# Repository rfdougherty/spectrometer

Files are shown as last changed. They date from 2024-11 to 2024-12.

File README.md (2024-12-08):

# Spectrometer

An Arduino-based controller for the [Hamamatsu C12880MA](https://www.hamamatsu.com/us/en/product/optical-sensors/spectrometers/mini-spectrometer/C12880MA.html) mini spectrometer using the [ESP32-S3](https://www.espressif.com/en/products/socs/esp32-s3) microcontroller. The figure below shows measurements of daylight entering a window across a 2-hour period just a little after noon in Redwood City California on October 26th, 2024. A simple auto-integration time algorithm was used so the raw voltage readings were scaled by the integration time to show the luminance differences between readings as the sun moved across the sky. (See [examples/spectrum.ipynb](examples/spectrum.ipynb) for the code used to make this plot.)

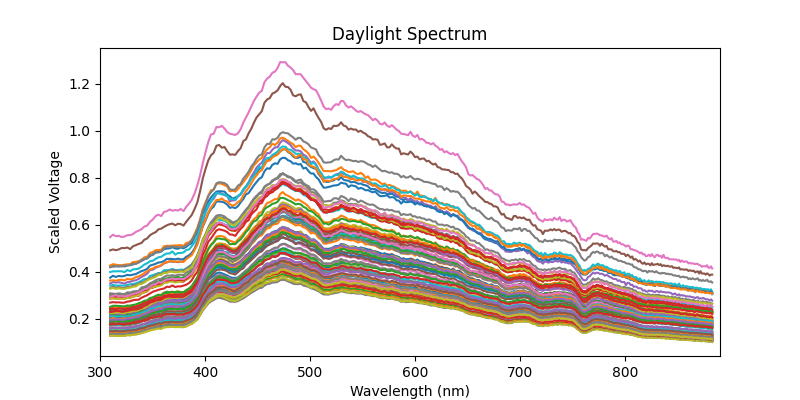
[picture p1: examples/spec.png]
example spectrum


## Overview

This project includes firmware for controlling the Hamamatsu C12880 mini spectrometer, offering web-based remote control and data acquisition. The system includes temperature and humidity monitoring via an AHT10 sensor. The device is very portable and easily powered for days using a small usb power bank, allowing longitudinal measurements in the field (e.g., to measure the daylight variation in a particular location).

### Features

- Web server interface for spectrometer control
- Over-the-Air (OTA) firmware updates
- WiFi configuration via WiFiManager
- Temperature and humidity data
- Wavelength calibration (be sure to update the coefficients in [getWavelength](firmware/firmware.ino) with the values from your calibration certificate!)
- NTP time synchronization for precise timestamping of measurements
- Status LED indicator

### Integration time

A spectrometer's integration time is the length of time it takes to collect photons and accrue charge on the sensor. It must be adjusted to maximize the signal-to-noise by using the full range of the sensor's analog output while avoiding saturation of any of the pixels. The current firmware does not include an automatic integration time algorithm, so the integration time must be manually set when you call the API to get a reading. The [examples/spectrum.ipynb](examples/spectrum.ipynb) notebook includes an example of how to use the API to automatically select an integration time by making multiple API calls with different integration times to find a value just below the sensor's saturation point.

## Hardware

- **Microcontroller**: ESP32-S3 (e.g., [LOLIN S3 mini](https://www.wemos.cc/en/latest/s3/s3_mini.html))
- **Spectrometer**: [Hamamatsu C12880MA](https://www.hamamatsu.com/us/en/product/optical-sensors/spectrometers/mini-spectrometer/C12880MA.html)
- **Temperature/Humidity Sensor**: AHT10/AHT20 (e.g., [this module](https://www.amazon.com/gp/product/B092495GZJ))
- **Connections**:
  - SPEC_TRG (output): GPIO 12 (requires voltage divider)
  - SPEC_ST (input): GPIO 13 (direct connection)
  - SPEC_CLK (input): GPIO 16 (direct connection)
  - SPEC_EOS (output): GPIO 11 (requires voltage divider)
  - SPEC_VIDEO (output): GPIO 10 (requires voltage divider; see note below)
  - I2C: SDA (GPIO 35), SCL (GPIO 36) (direct connection to the AHT10)

  You can buy a C12880 module and breakout board from [GroupGets](https://groupgets.com/products/hamamatsu-c12880ma-breakout-board). Their board offers level shifters and a buffer for the analog output of the spectrometer. However, the C12880 inputs can be driven directly from the microcontroller as they are rated for a 3V HIGH threshold. You do need to level-shift the digital outputs from the C12880 to avoid damaging the microcontroller. However, this can be easily achived with a simple 2-resistor [voltage divider](https://randomnerdtutorials.com/how-to-level-shift-5v-to-3-3v/). I used a 5K/10K pair. The S3 analog input is high impedance and does not need a buffer (but *does* need a divider; see notes below). Given this, I picked up a C12880 (with calibration certificate) from ebay for under $200 and built a simple breakout board with spare parts. (A schematic and pcd files for the breakout are coming soon!)

### Analog notes
The ESP32 had [notoriously bad](https://www.reddit.com/r/esp32/comments/1dgjxtm/honest_question_why_is_the_adc_so_bad_non_rant/) ADC performance, but the ESP32-S3 has a much improved ADC. I did some preliminary tests using an external [12-bit SPI ADC](https://www.microchip.com/en-us/product/mcp3204), an [op-amp buffer](https://www.ti.com/lit/ds/symlink/opa344.pdf?ts=1731079872575), and a simple voltage divider to read the C12880 analog output but the results were actually *more* noisy than using the S3's ADC with no buffer and just a 2-resistor divider. Take this external ADC test with a grain of salt, as this was done on a breadboard, so it's quite possible that a well-designed PCB could yield better results with an external ADC. But for my purposes, the simplest solution was good enough to achieve very stable spectrometer readings. Also note that unlike the divider for the digital pins, I paid careful attention to the exact resistance values to achive a full-range ADC input of [0-3.1V](https://docs.espressif.com/projects/esp-idf/en/v4.4.3/esp32s3/api-reference/peripherals/adc.html) and measured a bunch of individual resistors to pick a pair that got me closest to <= 3.1V (e.g., a 2K that measures a bit high and a 3.3K that measures a bit low). Adding a small (0.1nF) filter capacitor helped with stability.

## Firmware

Note that the C12880 wavelenths are individually calibrated and thus you should receive a calibration certificate with your spectrometer. You must update the coefficients in [getWavelength](firmware/firmware.ino) with the values from your calibration certificate to get accurate data.

The web API returns json payloads. To keep things simple and fast, I used snprintf to build the JSON payload strings. This works well for now, but will not be the easiest to maintain if the API is expanded. In that case, this code should be refactored to use a proper JSON library like [ArduinoJson](https://arduinojson.org/).

The firmware code uses the following Arduino libraries:
- [Streaming](https://github.com/janelia-arduino/Streaming)
- [AHTxx](https://github.com/m5stack/AHTxx)
- Custom C12880 library (included in this repo)

### C12880 clock pulses
The code uses simple bit-banging to drive the C12880 which imposes some limits on how fast it can run and thus the minimum integration time that can be achieved. I did explore other options and implemented one (RMT; see notes below) but found that given the somehat involved C12880 requirement that the clock pin, read start pin, and analog video out pin need to be coordinated the RMT would not be a good solution. So to make the bit-banging fast, I use [direct register settings](https://www.reddit.com/r/esp32/comments/f529hf/results_comparing_the_speeds_of_different_gpio/) to save the digitalWrite overhead. I also implemented a sub-microsecond delay function that counts CPU clock ticks. The latter was critical for getting fast reads (and thus short integration times) as delayMicros has a theoretical minimum delay of 1 microsecond, but in practice averages about 2-3 microseconds due to rounding and overhead.

### ADC Reads
I originally used [ESP32-S3-FastAnalogRead](https://github.com/stg/ESP32-S3-FastAnalogRead) to speed up single-shot analog reads, but that package is out of date and throws runtime errors when compiled with ESP-IDF 5 (aka Arduino in ESP-Arduino 3.x). Also, the new IDF has improved the analogRead functions and thus closed the gap with hand-optizied code. I did explore using continuous ADC reads and found that to be about 2x faster than single-shot reads, but I couldn't be confident that the readings were perfectly synchronized with each C12880 pixel and it may have been off by one or two pixels, so I reverted to using a simple sing-shot ADC read approach. This results in about a 10 millisecond readout time. However, unlike the clok pulses, this does not affect the minimum integration time and merely adds an extra 5ms delay between measurements, which seems worth the tradeoff for more reliable readings.

## Examples

See the [Jupyter](https://jupyter.org/) notebook in [examples](examples) for a simple example of how to read spectrum data from the spectrometer using python code.

## Configuration

The device uses WiFiManager for initial WiFi setup:
1. On first boot, the device creates an access point
2. Connect to the AP and configure your WiFi credentials
3. The device will automatically connect to your network on subsequent boots

## Usage

The device provides a web interface accessible via its IP address. Available endpoints:
- `/wavelength`: Get the calibrated wavelengths.
- `/spectrum/{integration_time}`: Acquire spectral data for a given integration time. (see python code for more details)
- `/pulserate/{pulse_rate}`: Set the spectrometer clock pulse rate, in Hz. Should be in the rante 100000 - 5000000.
- `/temperature`: Get the temperature and humidity.
- `/i2c`: Scan I2C bus for connected devices (useful for debugging I2C issues)

## Development

### TODO

- Improve performance by removing delayMicros in clock logic. The C12880 supports being clocked at up to 5MHz, but we are maxing out at less than 0.5MHz due to the use of delayMicros, which has a theoretical minimum delay of 1us, but in practice is about 1.5us. Options for removing this limit include:
  - ~~use a peripheral that can generate the pulses, like the RMT~~
  - [dedicated GPIO](https://docs.espressif.com/projects/esp-idf/en/latest/esp32s3/api-reference/peripherals/dedic_gpio.html)
  - implement a sub-microsecond delay 
  
  Of these, the first is likely to be the most performant and should be able to easily hit 5MHz with minimal CPU cycles. But the last option is the easilest to implement.

  UPDATE: I tried using RMT and found it didn't help speed things up much despite adding lots of complexity. 
  The main reason that it didn't help much is due to the fact that we need to bit-bang the clock pin for the ADC
  readout and switching the pin from RMT mode to digitalWrite mode was taking several hundrend microseconds.

- Add an API endpoint to set and store calibration coefficients
- Add an automatic integration time selection algorithm
- Add a web GUI
- Design a better enclosure

### Info
- Version: 0.3
- Author: Bob Dougherty
- Repository: https://github.com/rfdougherty

## License

MIT License

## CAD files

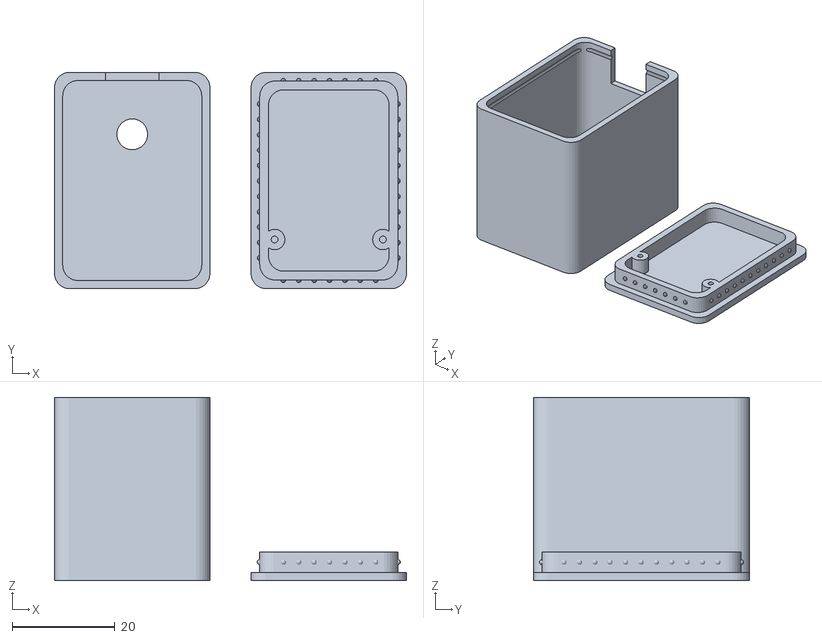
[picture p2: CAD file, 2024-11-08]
enclosure/spectrometer_box.stl
68.6 x 42.2 x 35.7

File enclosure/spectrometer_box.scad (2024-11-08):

/*
Suggested infill: 30%, triangles
  esp32: l=50, w=50, h=30
esp8266: l=45, w=35, h=30
*/


$fs=0.2;
e = 0.02;

// NOTE: length/width/height are exterior dimensions. Interior dimensions 
// are thick*2 smaller than these.
thick = 1.6;
length = 34 + thick*2 + 5;
width= 25 + thick*2 + 2.1;
height = 32 + thick*2 + 0.5;
cornerRad = 3;
slop = 0.1;
lidRimHeight = 4;
usbWidth = 10 + .5;
usbHeight = lidRimHeight + 5;

pillarRad = 2;
pillarSideOffset = 1; // offset from side of board + extra width/2
pillarEndOffset = 2 + 5; // offset from end of board + extra length
pillarHeight = lidRimHeight;

portOffset = 25 + 5.1;
portRad = 3;

// the rim on the lid will be a bit smaller than the box
lidThick = thick + 0.1;

snapRimRad = 0.5;
snapRimOffset = (thick + cornerRad) * 2;
snapRimDelta = 3; // the rims will be symmetric if this is a factor of width & length

centerWidth = width/2-cornerRad;

translate([cornerRad, cornerRad, 0]){
  difference() {
    union() {
      // The main box
      difference() {
        roundedBox(length, width, height, cornerRad);
        translate([thick, thick, thick+slop])
          roundedBox(length-thick*2, width-thick*2, height-thick+slop, cornerRad);
      }
    }
    // snap-rim (hollowed-out cyliner) on the short sides
    for(y=[thick-cornerRad, length-thick-cornerRad])
      translate([snapRimDelta-cornerRad-1, y, height-(lidRimHeight/2)])
        rotate([0, 90, 0])
          cylinder(r=snapRimRad, h=width-snapRimDelta*2+2);
    // snap-rim on the long sides
    for(x=[thick-cornerRad, width-thick-cornerRad])
      translate([x, snapRimDelta-cornerRad-1, height-(lidRimHeight/2)])
        rotate([-90, 0, 0])
          cylinder(r=snapRimRad, h=length-snapRimDelta*2+2);
    // viewport hole
    translate([-cornerRad+width/2, -cornerRad+portOffset, -e])
      rotate([0, 0, 90])
        cylinder(r=portRad, h=lidThick+e*10);
    // usb cut-out
    translate([width/2 - cornerRad, 
               length - cornerRad-thick/2, 
               height-usbHeight/2+e])
      cube([usbWidth, thick+2*e, usbHeight], center=true);
  }
}

// Make the lid
translate([width*2+5, cornerRad, 0]){
  mirror([1,0,0]) {
    union() {
      difference() {
        union() {
          roundedBox(length, width, thick, cornerRad);
          translate([lidThick, lidThick, 0])
            roundedBox(length-lidThick*2, width-lidThick*2, thick+lidRimHeight, cornerRad);
  
          // Add snap-rim spheres along short edges
          for(x=[-width/2+cornerRad*2 : snapRimDelta : width/2-cornerRad*2]) 
            for(y=[lidThick-cornerRad, length-lidThick-cornerRad])
              translate([x+width/2-cornerRad, y, thick+lidRimHeight/2])
                sphere(snapRimRad);
          // Add snap-rim spheres along long edges
          for(y=[-length/2+cornerRad*2 : snapRimDelta : length/2-cornerRad*2]) 
            for(x=[lidThick-cornerRad, width-lidThick-cornerRad])
              translate([x, y+length/2-cornerRad, thick+lidRimHeight/2])
                sphere(snapRimRad);
        }
        // Hollow-out lid
        translate([lidThick*2, lidThick*2, lidThick+slop])
          roundedBox(length-lidThick*4, width-lidThick*4, thick+lidRimHeight+slop, cornerRad);

      }
    }
      // pillars
      translate([-cornerRad + thick + pillarSideOffset + pillarRad, 
                 pillarEndOffset + thick - pillarRad, 
                 thick])
        difference() {
          cylinder(pillarHeight, r=pillarRad);
          translate([0, 0, e])
            cylinder(pillarHeight, r=pillarRad/3);
        }
      translate([width - cornerRad - thick - pillarRad - pillarSideOffset, 
                 pillarEndOffset + thick - pillarRad, 
                 thick])
        difference() {
          cylinder(pillarHeight, r=pillarRad);
          translate([0, 0, e])
            cylinder(pillarHeight, r=pillarRad/3);
        }
  }
}


module roundedBox(length, width, height, radius){
  dRadius = 2*radius;
  //base rounded shape
  minkowski() {
    cube(size=[width-dRadius,length-dRadius, height]);
    cylinder(r=radius, h=0.01);
  }
}

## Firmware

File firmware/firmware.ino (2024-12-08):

/*
 * Controller for Hamamatsu C12880 mini spectrometer:
 * https://www.hamamatsu.com/us/en/product/optical-sensors/spectrometers/mini-spectrometer/C12880MA.html 
 * 
 * Ideal board is an esp32-S3 as it has an improved ADC. I used a LOLIN S3 mini (4MB flash, 2MB PSRAM).
 * board def: ~/Library/Arduino15/packages/esp32/hardware/esp32/2.0.11/variants/lolin_s3_mini/pins_arduino.h
 * Note: to get serial output, enable "USB CDC On Boot" in the tools menu.
 *
 * API:
 *   /wavelength
 *   /spectrum/[int_time]
 *   /rmtfreq/[rmt_freq]
 *   /temperature
 *   /i2c
 * 
 * Bob Dougherty (https://github.com/rfdougherty) 2024.05.04
 *
 */
#include <WiFi.h>
#include <WebServer.h>
#include <uri/UriBraces.h>
#include <ArduinoOTA.h>
#include <Streaming.h>
#include <time.h>
#include <AHTxx.h>
#include <WiFiManager.h> // https://github.com/tzapu/WiFiManager
#include "c12880.h"
//#include <Wire.h>
//#include <ESPmDNS.h>

#define VERSION_STRING "Spectrometer 0.3"
#define STAT_LED LED_BUILTIN // LED_BUILTIN is 21 on xiao s3, 13 on tft, and 47 on s3 mini
#define LED_ON HIGH // On most boards this is LOW

// Use pins < 32 so we can use a fast digital write
// GPIO.out_w1ts = ((uint32_t)1 << _CLK_pin);
// GPIO.out_w1tc = ((uint32_t)1 << _CLK_pin);
#define SPEC_TRG 12 // 5
#define SPEC_ST  13 // 6
#define SPEC_CLK 16 // 9
#define SPEC_EOS  11 // 11
// ADC2 is used by the wifi, so be sure to use an adc1 pin (1,2,3,4,5,6,7,8,9,10,14)
#define SPEC_VIDEO 10

#define SDA_PIN 35 // 42
#define SCL_PIN 36 // 41

float g_temperature;
float g_humidity;

#define SPEC_CHANNELS 288
#define MAX_SAMPLES 20
uint16_t g_spec_data[SPEC_CHANNELS];
double g_nm_lut[SPEC_CHANNELS];

#define TIME_SYNC_TIMEOUT_MS 500 // getLocalTime is called often, so reduce the default timeout from 5s to .5s
const char* g_ntpServer = "pool.ntp.org";
const char* g_timezone = "PST8PDT,M3.2.0,M11.1.0";
struct tm g_timeinfo;

char g_mac_str[18]; // 12 digits, 5 colons, and a '\0' at the end
String g_ipaddr;
long g_first_boot_epoch_secs;

// need a char buffer big enough to hold data payload, where each sample needs at most 6 chars
// {"ts":1712435572,"spec":[1000,2000,...]}
char g_buf[SPEC_CHANNELS * 6 + 100];

WebServer server(80);

AHTxx aht10(AHTXX_ADDRESS_X38, AHT1x_SENSOR); //sensor address, sensor type
C12880_Class spec(SPEC_TRG, SPEC_ST, SPEC_CLK, SPEC_VIDEO);

void setup(){
  Serial.begin(115200); // Baud Rate set to 115200
  delay(100);
  Serial << F("Booting ") << VERSION_STRING << "\n";

  startWifi();
  Serial.println("Configuring time...");
  initTime(g_timezone);
  updateTime(5000); 
  setupRouting();
  Serial.println("HTTP server started");
  startOTA();
  Serial.println("OTA begun");

  if(aht10.begin() != true) {
    Serial << F("AHT10 sensor failed to start!") << "\n";
  } else {
    g_temperature = aht10.readTemperature(); // read 6-bytes via I2C, takes 80 milliseconds
    g_humidity = aht10.readHumidity(AHTXX_USE_READ_DATA);
    Serial << F("AHT10 sensor initialized; temp=") << g_temperature << F("C, hum=") << g_humidity << "%\n";
  }

  Serial.println(F("Beginning spectrometer"));
  spec.begin();
  Serial << F("Minimum integration time: ") << spec.get_min_iteg_us() << F(" microseconds.\n");
  for (int i=0; i<SPEC_CHANNELS; i++){
    g_nm_lut[i] = getWavelength(i);
  }
  g_first_boot_epoch_secs = getEpochSecs();
  delay(1000);
}

void loop(){
  static uint32_t last_update = 0;
  uint32_t ticks;
  ArduinoOTA.handle();
  server.handleClient();
  //updateTime(); // only need to do this when we use the time
  if (Serial.available() > 0) {
    char cmd = Serial.read();
    switch(cmd) {
      // for quick testing at a few different integration times and pulse rates
      case 's':
        readSpecToGbuf(100);
        Serial << g_buf << F("\n");
        break;
      case 'm':
        readSpecToGbuf(1000);
        Serial << g_buf << F("\n");
        break;
      case 'l':
        readSpecToGbuf(10000);
        Serial << g_buf << F("\n");
        break;
      case 'f':
        ticks = spec.set_pulse_rate(5000000);
        Serial << F("Pulse rate set to 5000000, ticks=") << ticks << F(", min_integration=") << spec.get_min_iteg_us() 
               << F("ns, CPU freq=") << getCpuFrequencyMhz() << F("MHz\n");
        break;
      case 't':
        ticks = spec.set_pulse_rate(500000);
        Serial << F("Pulse rate set to 500000, ticks=") << ticks << F(", min_integration=") << spec.get_min_iteg_us() 
               << F("ns, CPU freq=") << getCpuFrequencyMhz() << F("MHz\n");
        break;
      case '\n':
        break;
      default:
        Serial << F("Unknown command '") << cmd << F("'.\n");
    }
  }
  heartbeat('b');
  yield();
}

double getWavelength(uint16_t pixnum) {
  // Convert pixel number to wavelength using the 5th order polynomial calibration function
  const double a0=3.096674805e+2;
  const double b1=2.735884054;
  const double b2=-1.945647682e-3;
  const double b3=-5.627850896e-7;
  const double b4=-1.784036917e-8;
  const double b5=4.22796801e-11;
  double nm = a0 + b1*pixnum + b2*pow(pixnum,2) + b3*pow(pixnum,3) + b4*pow(pixnum,4) + b5*pow(pixnum,5);
  return nm;
}

void heartbeat(char color) {
  // color must be 'r', 'g' or 'b'
  static uint32_t prev_millis;
  static uint32_t prev_blink_millis;
  static uint8_t led_on;
  const uint32_t flash_interval = 3000;
  const uint8_t on_ms = 3;
  const uint8_t bright = 10;
  uint32_t cur_millis = millis();

  if(led_on){
    if(cur_millis - prev_blink_millis > on_ms){
      rgbLedWrite(RGB_BUILTIN, 0, 0, 0);
      led_on = false;
      prev_blink_millis = cur_millis;
    }
  }else{
    if(cur_millis - prev_millis > flash_interval){
      switch(color){
        case 'g':
          rgbLedWrite(RGB_BUILTIN, 0, bright, 0);
          break;
        case 'b':
          rgbLedWrite(RGB_BUILTIN, 0, 0, bright);
          break;
        default:
          rgbLedWrite(RGB_BUILTIN, bright, 0, 0);
      }
      
      led_on = true;
      prev_millis = cur_millis;
      prev_blink_millis = cur_millis;
    }
  }
}

void startOTA() {
  ArduinoOTA
    .onStart([]() {
      String type;
      if (ArduinoOTA.getCommand() == U_FLASH)
        type = "sketch";
      else // U_SPIFFS
        type = "filesystem";

      // NOTE: if updating SPIFFS this would be the place to unmount SPIFFS using SPIFFS.end()
      Serial.println("Start updating " + type);
    })
    .onEnd([]() {
      Serial.println("\nEnd");
    })
    .onProgress([](unsigned int progress, unsigned int total) {
      Serial.printf("Progress: %u%%\r", (progress / (total / 100)));
    })
    .onError([](ota_error_t error) {
      Serial.printf("Error[%u]: ", error);
      if (error == OTA_AUTH_ERROR) Serial.println("Auth Failed");
      else if (error == OTA_BEGIN_ERROR) Serial.println("Begin Failed");
      else if (error == OTA_CONNECT_ERROR) Serial.println("Connect Failed");
      else if (error == OTA_RECEIVE_ERROR) Serial.println("Receive Failed");
      else if (error == OTA_END_ERROR) Serial.println("End Failed");
    });
  ArduinoOTA.begin();
}

void i2c_scan(char *output, size_t output_size) {
  byte error, address;
  int nDevices = 0;
  size_t written = 0;

  written += snprintf(output + written, output_size - written, "{\"devices\":[");

  for(address = 1; address < 127; address++ ) {
    Wire.beginTransmission(address);
    error = Wire.endTransmission();
    
    if (error == 0) {
      written += snprintf(output + written, output_size - written, 
                          "{\"num\":%d,\"address\":\"0x%02X\"}", nDevices, address);
      nDevices++;
    }
    else if (error == 4) {
      written += snprintf(output + written, output_size - written, 
                          "{\"num\":%d,\"address\":\"0x%02X\",\"error\":\"unknown\"}", nDevices, address);
    }
    
    if (written >= output_size - 1) {
      break; // Stop if we're about to overflow the buffer
    }
  }
  written += snprintf(output + written, output_size - written, "]}");
}

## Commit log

2024-11-08 Inital commit
    [spectrometer_box.scad, spectrometer_box.stl]
2024-11-13 Remove fastAnalogRead
    Refactored code to remove dependence on S3-FastAnalogRead. I don't
    think that code was necessary with the overhauled ADC API in
    ESP-IDF 5 (available for Arduino in ESP-Arduino 3.x). The code
    now uses the continuous ADC API, which is over 2x faster than
    single-shot using readAnalog. It reads 288 samples in under 5ms.
    Now the main performance limitation is the clock. The C12880 supports
    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
